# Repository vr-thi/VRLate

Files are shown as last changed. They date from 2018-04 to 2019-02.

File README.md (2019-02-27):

# VRLate
Tool to measure motion-to-photon and mouth-to-ear latency in distributed VR-Systems. For more information have a look at the [paper](https://arxiv.org/abs/1809.06320 "paper") presented at the [15th workshop on VR and AR of the Gesellschaft für Informatik e.V. 2018](https://www.givrar2018.de/).

## Overview
Compared to existing measurement techniques, the described method is specially designed for distributed VR systems. It will help to evaluate different setups in terms of motion-to-photon and mouth-to-ear latencies. The game-engine *Unity 3D* is used to simulate the virtual world. The following two figures demonstrate how the system works. 

<p>
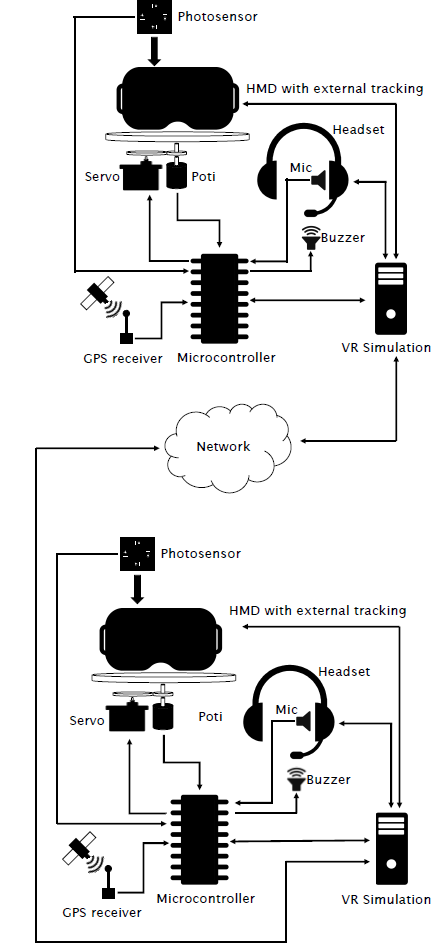
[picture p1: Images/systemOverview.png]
  
  
</p>

Two distributed measurement systems are synchronized via a GPS timepules. At both stations the motion-to-photon latency and the mouth-to-ear latency is measured via a potentiometer, photodiodes, piezo buzzers, and microphones. For more information please read the [paper](https://arxiv.org/abs/1809.06320 "paper").

## Hardware
The hardware setup of the system is shown in the following picture. All circuits are drawn with the open-source software *Fritzing* and are added to the [Fritzing folder]("/Fritzing/").

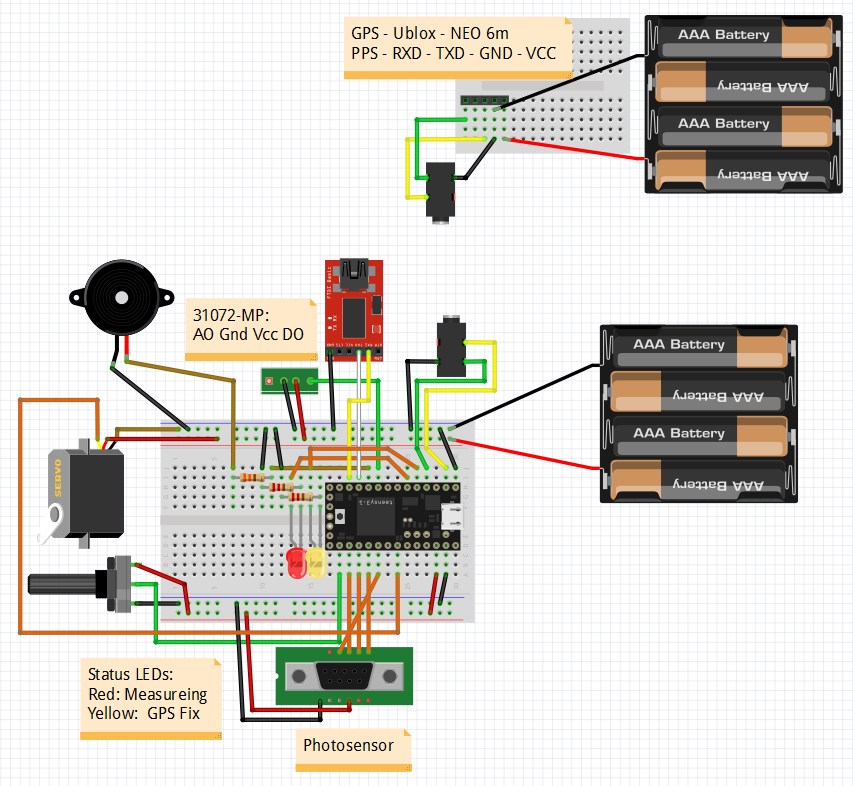
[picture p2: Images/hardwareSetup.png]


### Rotation platform
For the measurement setup, a potentiometer is used to continuously trace the rotation angle of the tracked object (e.g., an HMD). A servo connected to the microcontroller controls the platform rotary motion. With this setup, steady back-and-forth movements of the tracked object are possible.

### Photosensor
The photosensor is used to monitor display outputs and captures the rotary angle of the tracking system which is output in a brightness code. During measurement, right before the rendering process, the VR system outputs the last captured horizontal rotation angle in an encoded brightness code. The *TSL250R photosensors* was used to capture the screen brightness with the microcontroller. 

> Please Note that in the paper we described and used a photosensor with four *TSL250R* diodes. Further tests showed that the system could also be simplified by only using one diode. The Unity code was updated to work with one photodiode reading only.

## Software

To run the project the following software needs to be installed:

- **Arduino 1.8.8** IDE to compile the C++ code to the microcontroller. [link](https://www.arduino.cc/en/Main/OldSoftwareReleases "link")
- **Teensy Loader 1.45** Program used to allow the compilation of teensy code with the Arduino IDE. [link (windows)](https://www.pjrc.com/teensy/td_145/TeensyduinoInstall.exe)
- **Unity 3D 2017.1.1f1** Game engine [link](https://unity3d.com/de/get-unity/download/archive)
- **R** Statistics program [link](https://cran.r-project.org/bin/windows/base/). **RStudio** is recommended as IDE [link](https://www.rstudio.com/).
- **(optional) TTL Driver** Driver for used TTL adapter. Required to be installed manually for Windows 7. [link](https://www.jens-bretschneider.de/aktuelle-treiber-fur-seriell-zu-usb-adapter/)

## Quick Start

The project can be split in three components:

- **ArduinoIno** Contains all the microcontroller code.
- **Unity** Untiy 3D project to output the brightness code, take measurements and write the results to disk.
- **Parser** R script to parse the measurement results and calculate the end-to-end latency of the VR-system.

### Setup 
Both USB-ports of the *Teensy 3.2* bust be connected to the PC. The built-in mini-USB-port is used to program and debug the microcontroller. The other USB to TTL adapter is used to communicate between the Unity instance and the external microcontroller. Before you can start using the hardware you have to compile and upload the C++ code. Start the Arduino IDE and select the *Teensy 3.2* board. Also make sure that the correct USB-interface and Port is selected (see the following screenshots).

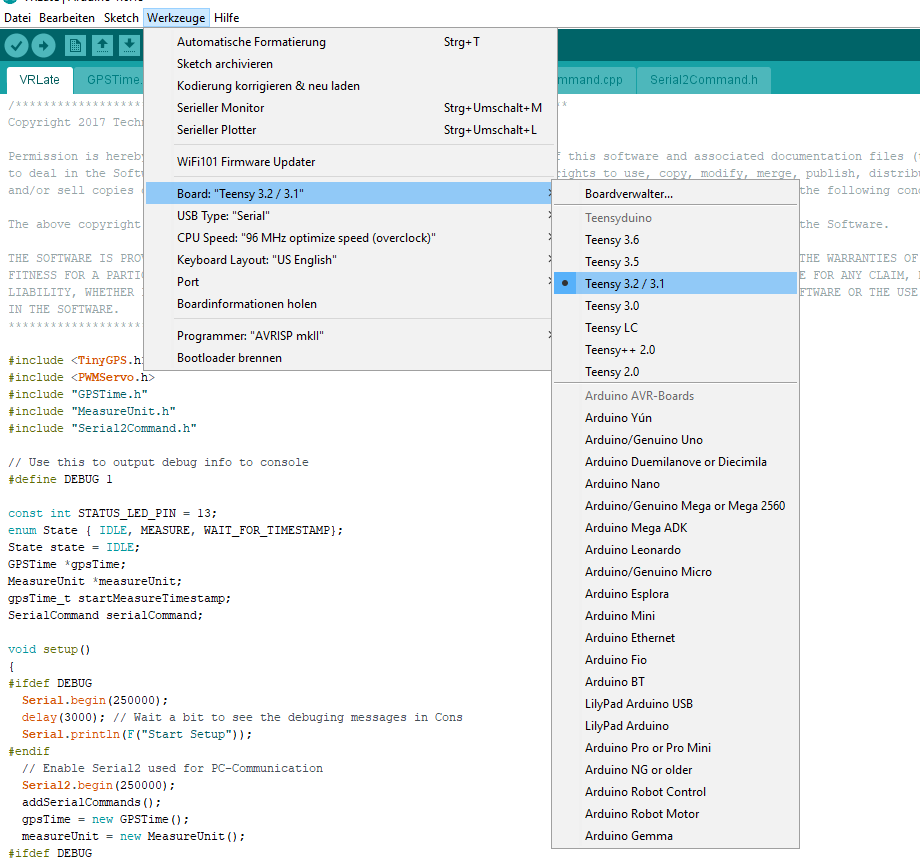
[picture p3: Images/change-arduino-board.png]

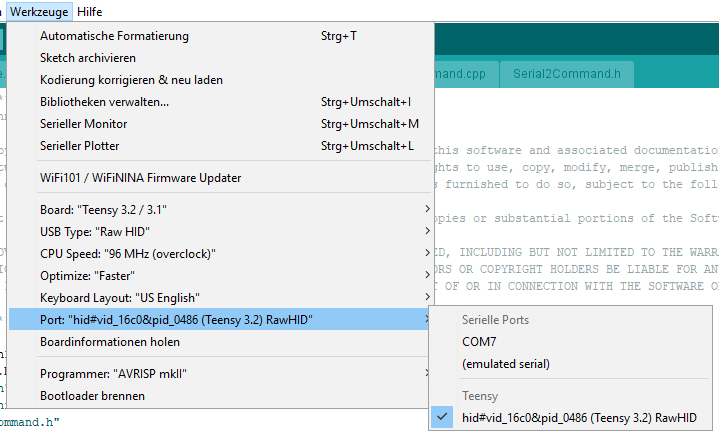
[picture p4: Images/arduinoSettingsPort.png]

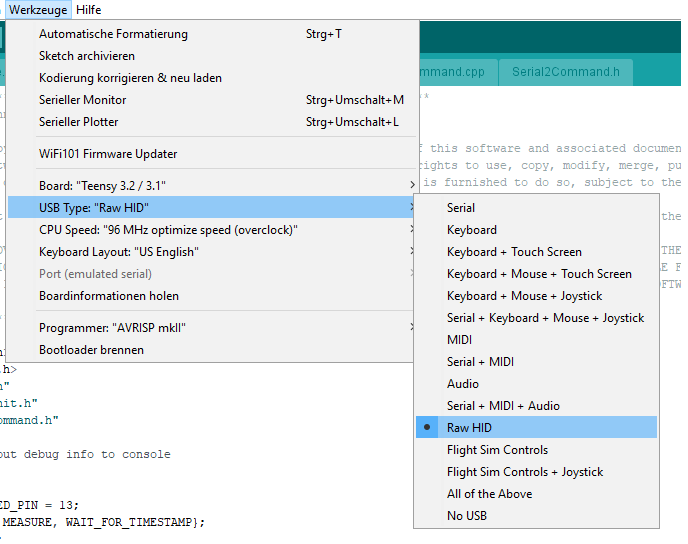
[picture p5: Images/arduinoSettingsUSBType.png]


Another very important setting that needs to be adjusted is the optimizer. Make sure that the Arduino compiler optimizes for smallest code. See next image for details:

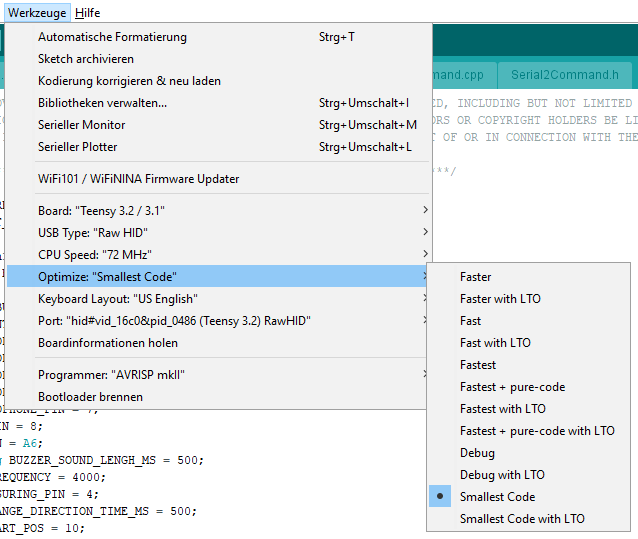
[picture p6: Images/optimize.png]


After the controller is powered via the USB-Port, the second USB->TTL adapter should be visible to the windows operating system. Open the device manager and check that a COM port is open. 

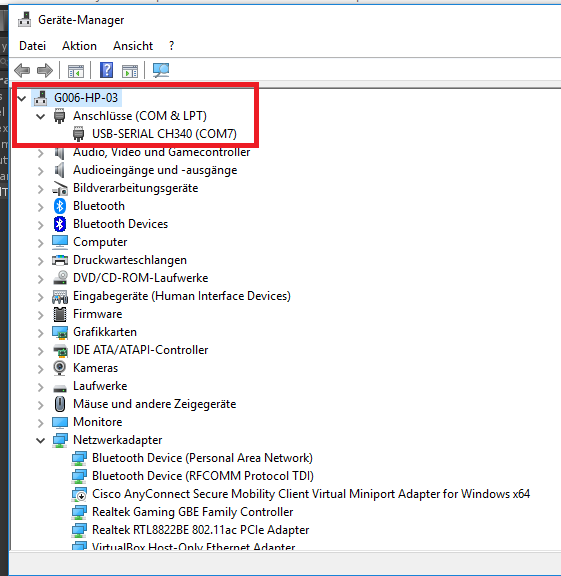
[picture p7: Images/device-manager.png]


Compile and upload the VRLate code via the Arduino IDE. 

### Run 

After the hardware is setup, the teensy microcontroller needs to be connected with the computer running the VR simulation. Within the provided Unity project open the *VRLate* scene. There is only one parent game object (*camera*) which has the VRLate script attached to it. All necessary settings must be set in this script instance.

Please make sure that Unity and teensy are connected correctly and check if the right serial port is set in the *VR Late script* (default is COM4). Run the Unity project and check whether error messages occur. If so, recheck the wiring and make sure that the baud rate is set correctly (default is 250000). 

If no error message occurs, you can start taking measurements. Run the Unity project and hit *F1* to start measurement. If no servo motor is connected to the microcontroller you then have to rotate the HMD mounted on the potentiometer back and forth manually. 

If you have two distributed systems which are synchronized via a valid GPS timestamp, you can press *F2* on both stations and the measurement will start at the next full minute. 

After measurement, Unity outputs CSV files to the designated folder (set output directory in *VRLate script*). The provided [R-script](/Parser/VRLate.r) can then be used to retrieve the motion-to-photon delay via cross-correlation.

## Citation
If you use this project for your research, please consider citing:

    @article{Becher.2018,
         author = {
            Becher, Armin 
            and Angerer, Jens 
            and Grauschopf, Thomas},
         title = {Novel Approach to Measure Motion-To-Photon and Mouth-To-Ear Latency in Distributed Virtual Reality Systems},
         publisher = {Shaker},
         isbn = {978-3-8440-6215-1},
         series = {Berichte aus der Informatik},
         editor = {Herder, Jens and Geiger, Christian and D{\"o}rner, Ralf and Grimm, Paul},
         booktitle = {Virtuelle und Erweiterte Realit{\"a}t},
         year = {2018},
         address = {Herzogenrath}
    }

## License

This project is licensed under the MIT License - see the [LICENSE.md](LICENSE.md) file for details.

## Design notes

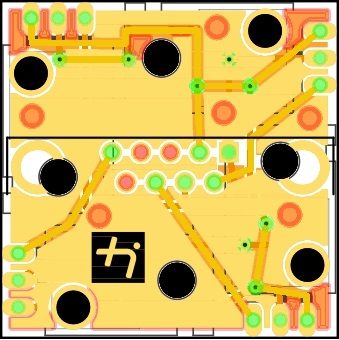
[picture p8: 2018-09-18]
Images/photodiodes_diagram.jpg

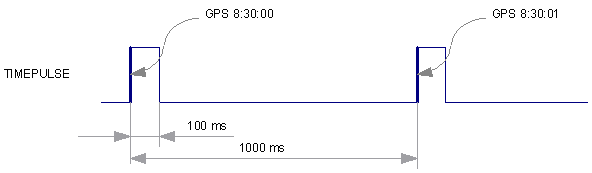
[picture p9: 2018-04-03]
Images/gpsTimepulse.png

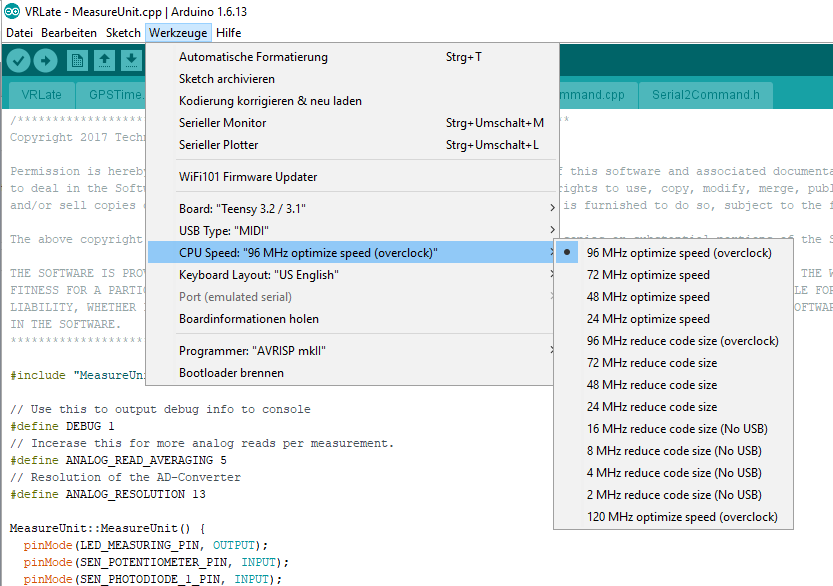
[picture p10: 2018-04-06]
Images/arduinoSettings.png

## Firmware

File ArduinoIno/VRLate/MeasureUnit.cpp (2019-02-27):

/*******************************************************************************
Copyright 2017 Technische Hochschule Ingolstadt

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
The above copyright notice and this permission notice shall be included in all copies or substantial portions of the Software.

THE SOFTWARE IS PROVIDED "AS IS", WITHOUT WARRANTY OF ANY KIND, EXPRESS OR IMPLIED, INCLUDING BUT NOT LIMITED TO THE WARRANTIES OF MERCHANTABILITY, 
FITNESS FOR A PARTICULAR PURPOSE AND NONINFRINGEMENT. IN NO EVENT SHALL THE AUTHORS OR COPYRIGHT HOLDERS BE LIABLE FOR ANY CLAIM, DAMAGES OR OTHER 
LIABILITY, WHETHER IN AN ACTION OF CONTRACT, TORT OR OTHERWISE, ARISING FROM, OUT OF OR IN CONNECTION WITH THE SOFTWARE OR THE USE OR OTHER DEALINGS 
IN THE SOFTWARE.
***********************************************************************************/

#include "MeasureUnit.h"

// Use this to output debug info to console
#define DEBUG 1 
// Increase this for more analog reads per measurement.
#define ANALOG_READ_AVERAGING 5
// Resolution of the AD-Converter
#define ANALOG_RESOLUTION 13

MeasureUnit::MeasureUnit() {
  pinMode(LED_MEASURING_PIN, OUTPUT);
  pinMode(SEN_POTENTIOMETER_PIN, INPUT);
  pinMode(SEN_PHOTODIODE_1_PIN, INPUT);
  pinMode(SEN_PHOTODIODE_2_PIN, INPUT);
  pinMode(SEN_PHOTODIODE_3_PIN, INPUT);
  pinMode(SEN_PHOTODIODE_4_PIN, INPUT);
  pinMode(SEN_MICROPHONE_PIN, INPUT);
  pinMode(BUZZER_PIN,OUTPUT);
  digitalWrite(LED_MEASURING_PIN, LOW);
  servo.attach(SERVO_PIN);
  servo.write(SERVO_START_POS);
  canceled = false;
  valuesInBuffer = 0;
  numberOfMeasureintervals = 5000;
  measureCounter = 0;
  measureInterval_us = 1000; // Default measure interval timespan
  analogReadResolution(ANALOG_RESOLUTION); // The Teensy 3.2 has a 13 bit resolution ADC
  analogReadAveraging(ANALOG_READ_AVERAGING); // Reduce Signal Noise
}

void MeasureUnit::begin() {
#ifdef DEBUG
  Serial.println(F("Begin measurement"));
#endif
  previousDirectionChange_ms = 0;
  servo.write(SERVO_END_POS);
  updateRotationPlatform();  
  valuesInBuffer = 0;
  measureCounter = 0;
  previousMeasure_us = micros();
  digitalWrite(LED_MEASURING_PIN, HIGH);  
  tone(BUZZER_PIN, BUZZER_FREQUENCY);
  unsigned long startMeasureTime = millis();
  audioDelay = -1;
  while(millis() - startMeasureTime < BUZZER_SOUND_LENGH_MS){
    // Check if Delay was Zero  
    int audioReading = digitalRead(SEN_MICROPHONE_PIN);
    if(audioDelay < 0 && audioReading == HIGH){
      audioDelay = millis() - startMeasureTime;
#ifdef DEBUG
  Serial.print(F("Set audio delay to: "));
  Serial.println(audioDelay);
#endif      
    }
  }
  noTone(BUZZER_PIN);
  measure();
}

void MeasureUnit::cancel() {
  finishMeasurement();
  canceled = true;  
}

void MeasureUnit::measure() {
  int arrLength = 5;
  uint16_t arr[arrLength];
  delayMicroseconds(10);
  arr[0] = analogRead(SEN_POTENTIOMETER_PIN);  
  delayMicroseconds(10);
  arr[1] = analogRead(SEN_PHOTODIODE_1_PIN);
  delayMicroseconds(10);
  arr[2] = analogRead(SEN_PHOTODIODE_2_PIN);
  delayMicroseconds(10);
  arr[3] = analogRead(SEN_PHOTODIODE_3_PIN);
  delayMicroseconds(10);
  arr[4] = analogRead(SEN_PHOTODIODE_4_PIN);
  pushOnBuffer(arr, arrLength);
  int audioReading = digitalRead(SEN_MICROPHONE_PIN);
  if(audioDelay < 0 && audioReading == HIGH){
    audioDelay = measureCounter + BUZZER_SOUND_LENGH_MS;
#ifdef DEBUG
  Serial.print(F("Set audio delay to: "));
  Serial.println(audioDelay);
#endif    
  }
  ++measureCounter;
}

void MeasureUnit::pushOnBuffer (const uint16_t *arr, int length) {
  if (valuesInBuffer + length <= BUFFER_SIZE) {
    for (int i = 0; i < length; i++) {
      buffer[valuesInBuffer] = arr[i];
      ++valuesInBuffer;
    }
  } else {
#ifdef DEBUG
    Serial.println(F("ERROR: Try to push values on buffer but it is full!"));
#endif
  }
}

bool MeasureUnit::update() {
  // Check if canceled
  if (canceled) {
#ifdef DEBUG
    Serial.println(F("User canceled measurement -> Go back to Idle state"));
#endif
    canceled = false;
    return false;
  }

  // Check if end of measurement
  if (measureCounter >= numberOfMeasureintervals) {
#ifdef DEBUG
    Serial.println(F("Finished Measurement -> Transmit data"));
#endif
    finishMeasurement();
    transmitData();
    return false;
  }
  
  // Check if need to measure
  unsigned long currentMicros = micros();
  if ((unsigned long)(currentMicros - previousMeasure_us) >= measureInterval_us) {
    measure();
    previousMeasure_us = currentMicros;
  }
    
  updateRotationPlatform();  
  return true;
}

// Send data to PC. 
// First Number is the audio delay
// Second is values in buffer. 
// Then (1 Poti, 4 Photo) * measure intervals
void MeasureUnit::transmitData() {
#ifdef DEBUG
  Serial.println(audioDelay);
#endif
  Serial2.println(audioDelay);  
#ifdef DEBUG
  Serial.println(valuesInBuffer);
#endif
  Serial2.println(valuesInBuffer);
  for (int i = 0; i < valuesInBuffer; ++i) {
#ifdef DEBUG
    Serial.println(buffer[i]);
#endif
    Serial2.println(buffer[i]);
  }
#ifdef DEBUG
  Serial.println(F("Finished transmission of measurement data to PC -> Go back to Idle state"));
#endif
}

void MeasureUnit::setNumberOfMeasureintervals(unsigned long n) {
  numberOfMeasureintervals = n;
#ifdef DEBUG
  Serial.print(F("Set Number of measure intervals to "));
  Serial.println(n);
#endif
}

// Cleanup and reset after finished measurement
void MeasureUnit::finishMeasurement(){    
    // Set servo to start pos
    servo.write(SERVO_START_POS);
    digitalWrite(LED_MEASURING_PIN, LOW);
}

// Check if need to rotate platform in other direction
void MeasureUnit::updateRotationPlatform(){
  unsigned long currentMillis = millis();
  if((unsigned long)(currentMillis - previousDirectionChange_ms) >= SERVO_CHANGE_DIRECTION_TIME_MS){
    int lastRotationDirection = servo.read();
    if(lastRotationDirection == SERVO_START_POS){
      servo.write(SERVO_END_POS);
    } else {
      servo.write(SERVO_START_POS);
    }
    previousDirectionChange_ms = currentMillis;
#ifdef DEBUG
    Serial.print(F("Changed direction. Last direction: "));
    Serial.println(lastRotationDirection);
#endif
  }  
}

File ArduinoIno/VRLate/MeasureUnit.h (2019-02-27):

/*******************************************************************************
Copyright 2017 Technische Hochschule Ingolstadt

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
The above copyright notice and this permission notice shall be included in all copies or substantial portions of the Software.

THE SOFTWARE IS PROVIDED "AS IS", WITHOUT WARRANTY OF ANY KIND, EXPRESS OR IMPLIED, INCLUDING BUT NOT LIMITED TO THE WARRANTIES OF MERCHANTABILITY, 
FITNESS FOR A PARTICULAR PURPOSE AND NONINFRINGEMENT. IN NO EVENT SHALL THE AUTHORS OR COPYRIGHT HOLDERS BE LIABLE FOR ANY CLAIM, DAMAGES OR OTHER 
LIABILITY, WHETHER IN AN ACTION OF CONTRACT, TORT OR OTHERWISE, ARISING FROM, OUT OF OR IN CONNECTION WITH THE SOFTWARE OR THE USE OR OTHER DEALINGS 
IN THE SOFTWARE.
***********************************************************************************/

#if !defined(MEASUREUNIT_H)
#define MEASUREUNIT_H

#include <Arduino.h>
#include <PWMServo.h>

#define BUFFER_SIZE 25002

const int SEN_POTENTIOMETER_PIN = A0;
const int SEN_PHOTODIODE_1_PIN = A1;
const int SEN_PHOTODIODE_2_PIN = A2;
const int SEN_PHOTODIODE_3_PIN = A3;
const int SEN_PHOTODIODE_4_PIN = A4;
const int SEN_MICROPHONE_PIN = 7;
const int BUZZER_PIN = 8;
const int SERVO_PIN = A6;
const unsigned long BUZZER_SOUND_LENGH_MS = 500;
const int BUZZER_FREQUENCY = 4000;
const byte LED_MEASURING_PIN = 4;
const int SERVO_CHANGE_DIRECTION_TIME_MS = 500;
const int SERVO_START_POS = 10;
const int SERVO_END_POS = 170;

class MeasureUnit {
  public:
    MeasureUnit();
    void begin(); 
    bool update(); // needs to be called in main loop during measurement. Return false if measurement is over
    void cancel();  // Cancel the current measure session
    void setNumberOfMeasureintervals(unsigned long nr);
  private:
    PWMServo servo;
    void measure();
    void finishMeasurement();
    void updateRotationPlatform();
    void pushOnBuffer (const uint16_t *arr, int length);
    void transmitData();
    uint16_t valuesInBuffer;
    uint16_t buffer[BUFFER_SIZE];
    uint16_t potiStartPos;
    bool canceled;
    unsigned long measureInterval_us;
    unsigned long numberOfMeasureintervals;
    unsigned long previousMeasure_us;
    unsigned long measureCounter;    
    unsigned long previousDirectionChange_ms;   
    long audioDelay;    
};
#endif

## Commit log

2018-09-18 Updated readme and added fritzing circute files
    [PhotodiodeSetup.fzz, VRLate.fzz]
2019-02-27 Simplified measurement. Only use one photosensor for evaluation. Remove whole calibration process
